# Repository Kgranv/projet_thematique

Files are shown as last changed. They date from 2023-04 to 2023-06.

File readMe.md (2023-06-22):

# Requirements :<br/>

## For Raspberry pi

- Raspberry Pi OS Lite (64-bit)
- Python 3.10
- Python Libraries :
  - numpy 1.22.2
  - pandas 1.4.1
  - feather-format 0.4.1

## For Windows (optional)

- Python 3.10
- Python Libraries :
  - numpy 1.22.2
  - pandas 1.4.1
  - feather-format 0.4.1
  - matplotlib 3.5.2

# RaspberryPi recommendation :<br/>

- RaspberryPi type : RaspberryPi-4 <br/>
- RaspberryPi name : raspberrypi-projetMOON <br/>
- piUser : projetMOON <br/>

# Useful command :<br/>

For windows with powershell :<br/>

- Connect to raspberryPi with SSH :<br/>
  <code>ssh piUser@piName</code><br/>
- Send file to raspberryPi :<br/>
  <code>scp dataToSend piUser@piName:/home/piUser/folderPath</code><br/>
- Retrieve file from raspberryPi :<br/>
  <code>scp piUser@piName:/home/piUser/FilePath localFilePath</code><br/>
  if you are already in localFilePath, replace localFilePath by ".\\"<br/>

For raspberry-pi terminal :<br/>

- View file in directory :<br/>
  <code>ls</code><br/>
- change directory :<br/>
  <code>cd directoryName</code><br/>
  if you want to go in parent folder change directoryName by ..
- remove file :<br/>
  <code>rm fileName</code><br/>
- read file :<br/>
  <code>cat fileToRead</code>
- start pyhton script<br/>
  <code>python script.py</code><br/>
- start experience script<br/>
  <code>nohup python experience.py ftrFile.ftr</code><br/>

# How to setup your raspberry-pi :<br/>

You need to use the Raspberry Pi Imager software available here : https://www.raspberrypi.com/software/<br/>
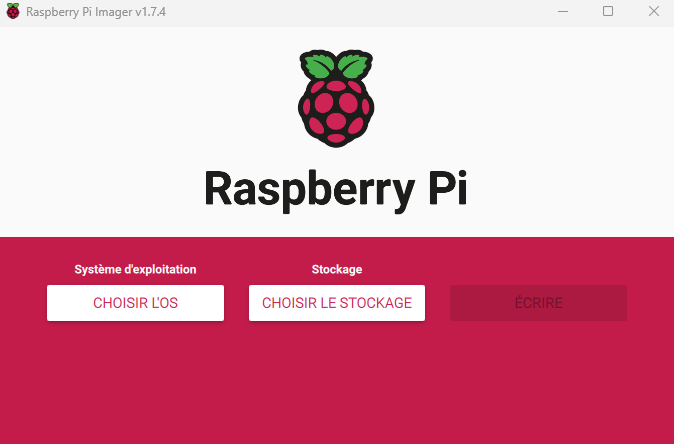
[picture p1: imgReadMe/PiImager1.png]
PiImagerPicture1


## Step 1 : Chose OS

You need to chose the Raspberry Pi OS Lite(64-bit). Don't use 32-bit OS because some library needs a 64-bit OS.<br/>
You can find it in Raspberry Pi OS (other) menu.
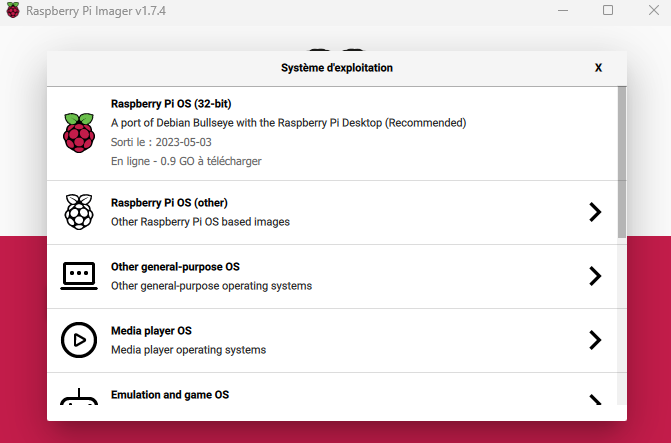
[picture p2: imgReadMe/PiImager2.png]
PiImagerPicture2

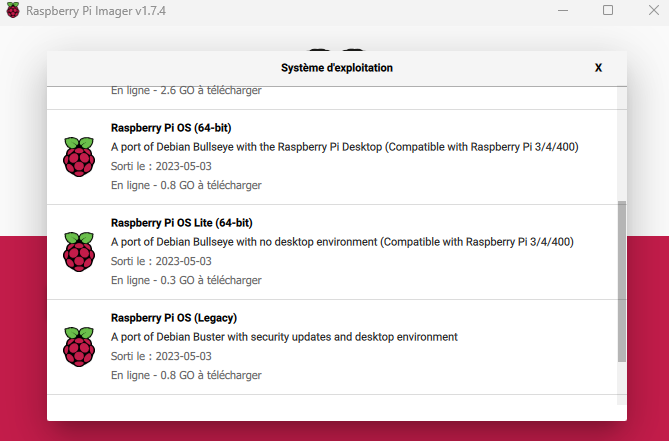
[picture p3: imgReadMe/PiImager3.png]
PiImagerPicture3


## Step 2 : Chose storage

Select the SD card you will use for the raspberry pi.

## Step 3 : Setup advance parameter

You need to change multiple parameter before writing the OS in the SD card :<br/>
You can find the parameter in the gear.<br/>

- Chose for all sessions in Image customization options
- Change the raspberry pi name<br/>
- Activate SSH : <br/>
  use authentification by password<br/>
- Define username and password<br/>
- Configurate the wifi<br/>

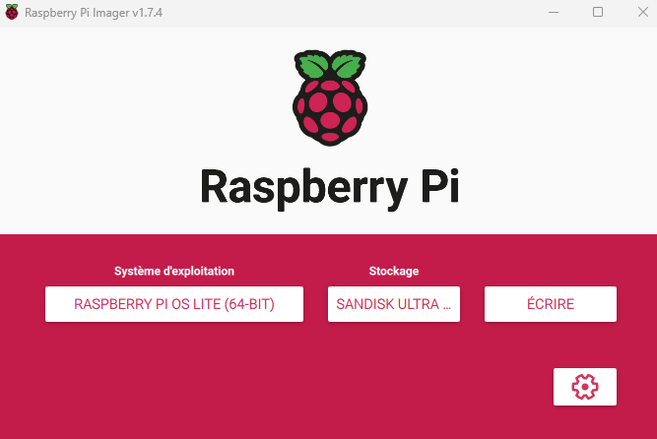
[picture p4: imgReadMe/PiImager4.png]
PiImagerPicture4

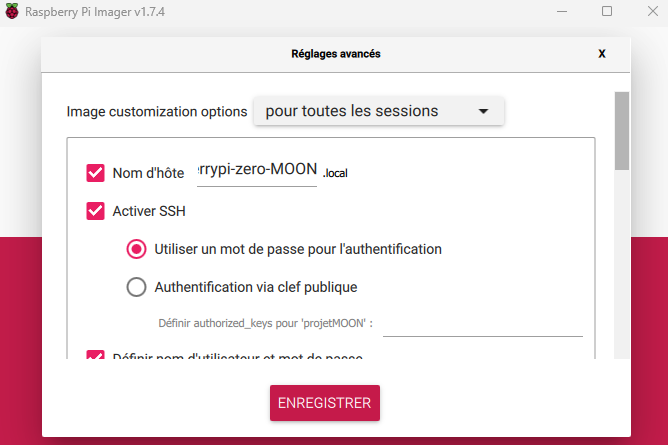
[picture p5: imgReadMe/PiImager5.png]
PiImagerPicture5

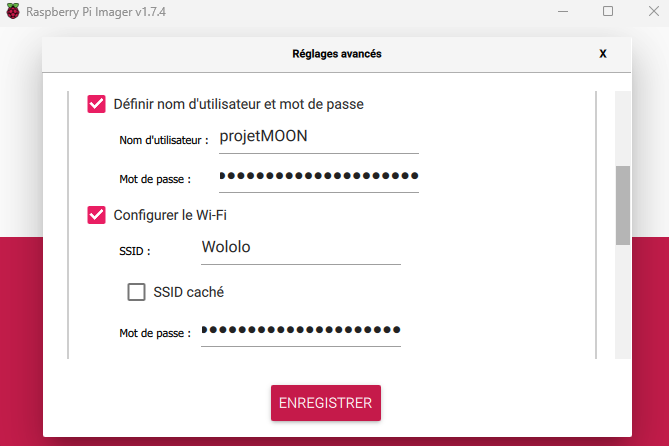
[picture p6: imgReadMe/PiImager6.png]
PiImagerPicture6


## Step 4 : Write on SD card

You can write the OS in the SD card and your OS it's ready !<br/>

## Step 5 : Install dependencies and Setup directory

You need to install dependencies.<br/>

- Connect to your raspberry pi via SSH :<br/>
  <code>ssh piUser@piName</code><br/>
  use the piUser and piName you have setup in step 3.<br/>
- Install OS update :<br/>
  <code>sudo apt update</code><br/>
  <code>sudo apt upgrade</code><br/>
- Install python :<br/>
  <code>sudo apt install python3.10</code>
- Install python library :<br/>
  <code>pip install numpy</code><br/>
  <code>pip install pandas</code><br/>
  <code>pip install feather-format</code><br/>
- Create directory :<br/>
  <code>mkdir data</code><br/>
  <code>mkdir userData</code><br/>

All the dependencies are installed you can close the SSH connection by closing the terminal.<br/>

## Step 6 : Transfert file on raspberry pi

You need to transfert all necessary file on raspberry pi.<br/>
Download following file from the repository :<br/>

- armerPompe.py<br/>
- controle.csv<br/>
- controle.py<br/>
- dataPreparation.py<br/>
- experience.py<br/>
- resetGPIO.py<br/>

repeat the following command for each file in the list to transfert to raspberry pi :<br/>

- Send file to raspberryPi :<br/>
  <code>scp fileToSend piUser@piName:/home/piUser</code><br/>

The setup of the raspberry pi is complete.

# Plug experience

## Motor

### Motor n°1

- red wire to Mosfet 1 Drain
- black wire to Mosfet 1 Source

### Motor n°2

- red wire to Mosfet 2 Drain
- black wire to Mosfet 2 Source

### Motor n°3

- red wire to Mosfet 3 Drain
- black wire to Mosfet 3 Source

## Electrovanne

### Electrovanne n°1

- wires to Mosfet 4 Drain/Source

### Electrovanne n°2

- wires to Mosfet 5 Drain/Source

### Electrovanne n°3

- wires to Mosfet 5 Drain/Source

## Raspberry pin

### Alimentation

- pin 4 (Alimentation 5V) to 5 V
- pin 6 (GND) to GND

### Motor

- pin 11 (GPIO 17) to Mosfet 1 Gate
- pin 13 (GPIO 27) to Mosfet 2 Gate
- pin 15 (GPIO 22) to Mosfet 3 Gate

### Electrovanne

- pin 29 (GPIO 5) to Mosfet 4 Gate
- pin 31 (GPIO 6) to Mosfet 5 Gate
- pin 33 (GPIO 13) to Mosfet 6 Gate

# Run an experience

## Step 1 : Prepare your data

The data need to be in csv file. The separator need to be ",".<br/>
Your data are presented like this :<br/>

| time | conc1 | conc2 |
| :--- | :---- | :---- |
| 0    | 1     | 1     |
| 2    | 6     | 8     |
| 10   | 2     | 1     |
| 15   | 4     | 2     |

time correspond of time from the start in second.<br/>
conc1 and conc2 it's the concentration of element at time t.

If you have download dataPreparation.py on your computer you can convert your data on your computer directly.
For convert your data directly on your computer follow the Step 3 before the Step 2.

## Step 2 : Transfert your data on raspberry pi

Transfert your data on the raspberry pi in the folder userData.<br/>
Open terminal in the folder of your data and use this command :<br/>
<code>scp dataToSend piUser@piName:/home/piUser/userData</code><br/>

If you have convert your data directly on your computer use this command instead :<br/>
<code>scp dataToSend piUser@piName:/home/piUser/data</code><br/>

## Step 3 : Convert your data

### If you have transfert your CSV file on raspberry pi

- Connect to your raspberry pi via SSH :<br/>
  <code>ssh piUser@piName</code><br/>
- run dataPreparation.py :<br/>
  <code>python dataPreparation.py</code><br/>
  Indicate the name of your data when ask.

Your data is now converted and placed in data.<br/>
The data converted is named by the date of creation like this:<br/>
year-moth-day_hourminsec.ftr

you can check the name of the data created in the folder data using :<br/>
<code>cd data</code><br/>
<code>ls</code><br/>
it will show all the data in the folder data.<br/>

### If you want convert your data on Windows

Before convert your data on Windows make sure you have the optionnal requirement on your computer.<br/>
Create 2 folder in directory of dataPreparation.py:<br/>

- userData<br/>
- data<br/>

Put your data to convert in userData folder.<br/>
Run dataPrepartion.py and indicate the name of your data when ask.<br/>
Your data is now converted and placed in data.<br/>
The data converted is named by the date of creation like this:<br/>
year-moth-day_hourminsec.ftr<br/>
You can check the data created using the script verificationFtr.py<br/>
Now you can do Step 2.

## Step 4 : Run experience

For start experience connect to raspberry pi if it's not already done :<br/>
<code>ssh piUser@piName</code><br/>
Run experience.py in background with :<br/>
<code>nohup python experience.py dataToUse.ftr</code><br/>
Close the terminal.<br/>
The Experience is running Step 5 and 6 will show you how to interact with experience.

## Step 5 : Control experience

If you want take sample or make an observation during the experience you need to suspend the process.

- Connect to raspberry pi :<br/>
  <code>ssh piUser@piName</code><br/>
- run controle.py
  <code>python controle.py</code><br/>
- Chose what you want to do :<br/>
  1. Sample<br/>
     For take a sample, you need to indicate which quantity you take.<br/>
  2. Observation<br/>
     For observe the cells.<br/>
  3. Restart cycle<br/>
     When you have finished your sample/observation restart the cycle.<br/>
  4. Log<br/>
     For see the last log of the experience.<br/>
  5. Stop<br/>
     Force stop of the experience if something goes wrong.<br/>
  6. Cancel<br/>
     Close controle.py<br/>

When you have finished dont forget to restart cycle and you can press cancel for close controle.py.<br/>

## Step 6 : Check log

- Connect to raspberry pi :<br/>
  <code>ssh piUser@piName</code><br/>
- Open the log:<br/>
  <code>cat output.log</code><br/>

For debug log use instead :<br/>
<code>cat nohup.out</code><br/>

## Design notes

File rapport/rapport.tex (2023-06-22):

% Basic info about your document: a4 paper, 11pt font size, article style.
\documentclass[a4paper, 11pt]{article}

\usepackage{graphicx} % Enables adding figures
\usepackage[a4paper, margin=18mm]{geometry} % Let's you adjust the margins
\usepackage[T1]{fontenc} % Font helvetica
\usepackage[scaled]{helvet}
\usepackage{authblk} % multiauthor
\usepackage{multirow} % table
\usepackage[table,xcdraw]{xcolor}
\usepackage{float} % position des figures,table
\usepackage[backend=biber,style=numeric,sorting=none]{biblatex} % bibliographie
\usepackage{fancyhdr} % footer
\usepackage{caption} % caption
\usepackage{multicol} % multicolonne
\usepackage{adjustbox}
\usepackage{pdfpages}

%Setup bibliographie
\addbibresource{bibliographie.bib} % utilise bibliographie.bib pour la bibliographie

%Setup figure
\graphicspath{ {./figure/} } % relative path for figure

\renewcommand\familydefault{\sfdefault} % set font for all document
\captionsetup[table]{name=Tableau} % Rename table
\renewcommand*\contentsname{Table des matières} % Rename table of contents
\setlength\parindent{0pt} % remove indent in new line

%Setup Titre, auteur et date
\title{
    \vspace{-2.5cm}
    \centering\\
    \centering\rule{17cm}{0.1mm}\vspace*{0.4in}\\
    \centering Projet thématique MOON}
\renewcommand\Authands{ et } % replace "and" by "et" in author
\author[1]{AYRINHAC Elisa}
\author[2]{DROUIN Clément}
\author[3]{JOUCLARD Charly}
\affil[1]{HEPIA, MT2, elisa.ayrinhac@hes-so.ch}
\affil[2]{HEPIA, MT2, clement.drouin@hes-so.ch}
\affil[3]{HEPIA, MT2, charly.jouclard@hes-so.ch}
\date{28 avril 2023}

%Setup header, footer
\pagestyle{fancy}
\fancyhead{} % clear all header fields
\renewcommand{\headrulewidth}{0pt} % no line in header area
\fancyfoot{} % clear all footer fields
\renewcommand{\footrulewidth}{1pt}
\newcommand{\changefont}{\fontsize{9}{11}\selectfont}
\newcommand{\TheAuthor}{AYRINHAC Elisa, DROUIN Clément, JOUCLARD Charly}
\fancyfoot[C]{\changefont\TheAuthor}
\fancyfoot[R]{\changefont\thepage}
\fancyfoot[L]{\changefont Projet thématique MOON}

\begin{document}

%Entete
\maketitle
\thispagestyle{empty}
\begin{center}
    \rule{\textwidth}{0.1mm}
\end{center}
%Introduction
\vspace{-1cm}
\section*{Introduction}
Ce rapport detail le projet thématique de deuxième année de bachelor
microtechnique de HEPIA option Bio-ingénierie.
Cette année notre cliente, Mme Loussert-Fonta Céline est une biologiste travaillante
sur l'endométriose, une maladie encore
peu connue mais très commune, touchant environ 1 femme sur 10.\\
Cette pathologie se caractérise par le développement du tissu semblable
à l'endomètre hors de l'utérus.
Ces tissus peuvent proliférer dans les organes voisins comme les ovaires;
l'intestin, la vessie ou même les poumons.
Les symptômes varient énormément entre les femmes mais ont retenu, le
plus souvent, celui de la douleur
extrême provoqué par la croissance de ces tissus.\\
Les objectifs du projet sont, d'une part, de mettre en application les
connaissances acquises durant nos études, mais également de développer de
nouvelles compétences comme la gestion de projet.
D'autre part, ce projet contribue à développer la recherche sur
l'endométriose et servira de support pour le \\
"project MOON : endoMetriosis Organoids to vOice up woman paiN".\\
Le but de notre projet est de créer un bio-chip qui permettrait d'étudier
les tissus de l'endomètre in vitro durant un cycle utérin. Cela signifie, imaginer, concevoir, fabriquer,
et tester un dispositif capable se recrée
les conditions d'un utérus (Température, humidité, concentration d'hormones, etc...)
\vspace{1cm}
\maketitle
\thispagestyle{empty}
\begin{center}
    \rule{\textwidth}{0.1mm}
\end{center}
\newpage
%Table des matieres
\tableofcontents
\newpage
%Debut rapport
\section{Etudes préliminaire}
\subsection{Biologie}
\subsubsection{Contexte}
Pour que l'expérience soit optimale, le client a besoin de suivre l'évolution d'un tissu d'endomètre sur la
durée d'un cycle endométrial.
Le système doit être compact et permettre l'observation des cellules en culture ainsi que la possibilité de
collecter des cellules et du milieu de culture pour analyse.
Afin mieux comprendre comment concevoir un appareil correspondant à la demande du client, une courte
introduction biologique est nécessaire.
\subsubsection{L'endomètre}
\begin{figure}[H]
    \centering
    \resizebox{0.5\linewidth}{!}{}
    \caption{Localisation de l'endomètre dans l'utérus}
    \label{fig:Schema_endomètre}
\end{figure}
L'endomètre est un épithélium qui compose une partie de l'appareil reproducteur féminin, il tapisse les
parois de la cavité utérine et est composé de 3 couches :
\begin{itemize}
    \item Le myomètre qui est la fondation de l'endomètre.
    \item la couche basale qui contient les glandes et les tissu conjonctifs.
    \item la couche fonctionnelle.
\end{itemize}
Cette dernière couche est celle qui vois sa taille changer durant le cycle menstruel.
\subsubsection{Le cycle menstruel}
"Le cycle menstruel est l'ensemble des phénomènes physiologiques,
survenant le plus souvent de façon périodique, qui préparent l'organisme de la femme à une éventuelle
fécondation.
La connaissance du cycle menstruel est importante pour aborder l'étude des troubles de la menstruation,
dans l'exploration de l'infertilité et dans la mise en œuvre des techniques de procréation médicalement
assistées."
\cite{Cycle_menstruel}\\
L'hypothèse émise par la biologiste serait qu'il y a corrélation en le cycle hormonal et l'apparition
de kystes dus à l'endométriose.
Durant le cycle utérin, le taux d'hormonal de la femme varie selon les jours. Cela permet
au corps de réguler la période de croissance de l'endomètre, puis de déclencher l'ovation et enfin
S'il n'y a pas eu fécondation, de déclencher les menstruations.
\begin{figure}[H]
    \centering
    \resizebox{0.5\linewidth}{!}{}
    \caption{Graphique montrant le cycle menstruel avec ces variation hormonal et ce que
        cela implique}
    \label{fig:Cycle menstruel}
\end{figure}
Comme vu dans la figure 2, les 4 hormones présentent dans le cycle sont :
\begin{itemize}
    \item La progestérone.
    \item Les estrogéne, notamment l'estradiol.
    \item La LH pour luteinizing hormone.
    \item La FSH pour follicle stimulating hormone.
\end{itemize}
La consigne est de reproduire les cycles de concentration de l'estradiol et de la progestérone.
Car ce sont les hormones suspectées dans l'apparition de l'endométriose. Cela signifie
recrée les conditions d'homéostasie des cellules ainsi que les conditions de
concentration de ce cycle et les appliquer à des cellules in vitro.
Afin de répondre au mieux à cette problématique un état de l'art de la culture
cellulaire sera établie ainsi qu'un inventaire des techniques présentent au campus biotech qui
pourraient être utile dans notre projet.
\newpage
\subsection{Etat de l'art}

\subsubsection{Incubateur}
Actuellement la culture cellulaire est un procédé connu et maitriser par l'Homme qui consiste à placer des cellules dans
un milieu de culture afin de les faire proliférer.
Cette méthode permet d'avoir des colonies de cellule pouvant aller jusqu'à former des organoïdes pouvant être utilisés
à des fins de recherche. Les organoïdes se comportant de manière similaire à l'organe miniaturisé.
Peu importe l'objectif, la méthode de culture garde toujours un objectif d'homéostasie et un objectif de prolifération. Dans la pratique cela revient
à placer dans un incubateur une colonie de cellules contenue dans un milieu nutritif.
Pour maintenir de bonnes conditions on place ces échantillons dans l'enceinte d'un incubateur qui permet d'isoler les cellules du milieu extérieur tout
en maintenant les constantes de températures, d'humidité et de CO2 de façon optimale.
Les incubateurs professionnels sont des machines de précision, asservis qui permettent de régler précisément toutes les conditions de leurs enceintes;
cela permet de chercher l'expression de certains phénotypes au sein des colonies.
Ils sont aussi dotés de sécurités notamment en matière de ventilation afin de protéger les cellules et le biologiste. Toutefois cette précision rend le matériel cher.
Il faut compter entre 5 000 CHF et 15 000 CHF pour un incubateur professionnel.
L'incubateur fait maison sont moins précise mais permette une personnalisation complète en matière de condition de culture.
Toutefois même si cela reste compliqué à construire dans sa totalité, il est assez simple de stabiliser la température et l'humidité.
Ces machines permettant de créer une atmosphère apte à la reproduction cellulaire toutefois il nous faut quelque chose qui contient les cellules et leur milieu nutritif.
il faut des instruments de culture biocompatible.
\subsubsection{Matériau biocompatible}
On appelle matériau biocompatible, les matériaux qui ont la capacité à ne pas interférer;
ne pas dégrader, le milieu biologique dans lequel ils sont utilisés. Dans notre cas, il faut
que le lieu d'accueil des cellules ne dégrade en rien leurs fonctionnements.
Actuellement les zones de culture sont
\begin{itemize}
    \item Les boites de pétris.
    \item Les écouvillons.
    \item La verrerie de chimie.
    \item Dans les labo d'HEPIA à la FCBG des biochip en PMMA, un polymere biocompatible.
\end{itemize}
Cette liste n'est pas exaustive, tout comptenant fait d'un matériau biocompatible peut en théorie
accueillir des cellules.
\subsubsection{Fluidique}
La fluidique est une partie importante dans la survie des cellules, c'est grace à elle que les
nutriments sont acheminés jusqu'à la zone de culture.
Elle se compose de tous les éléments comprenant du fluide, tel que :
\begin{itemize}
    \item Les réservoirs.
    \item Les pompes.
    \item les tuyaux.
    \item les vannes.
\end{itemize}
Les tuyaux utilisés à la FCBG sont de qualités médicales, c'est-à-dire qui sont biocompatibles. Ils ne diffusent pas
dans le milieu de culture, et ils ne sont pas sensibles aux méthodes de stérilisation.
\newpage
\subsection{Aperçu du projet}
\subsubsection{Besoins}
On peut voir avec la figure \ref{fig:bete_corne} que le système conçu va permettre au biologiste d'étudier l'influence des hormones sur du tissu endométrial.
\begin{figure}[H]
    \centering
    \resizebox{\linewidth}{!}{}
    \caption{Bête à corne}
    \label{fig:bete_corne}
\end{figure}
\subsubsection{Fonctions}
\begin{table}[H]
    \centering
    \begin{tabular}{|
            >{\columncolor[HTML]{CBCEFB}}l |l|}
        \hline
        \multicolumn{1}{|c|}{\cellcolor[HTML]{CBCEFB}\textbf{N°}} & \textbf{Fonction}                                 \\ \hline
        FP1                                                       & Maintenir les cellules en vie                     \\ \hline
        FP2                                                       & Intégrer des concentrations spécifiques d'hormone \\ \hline
        FC3                                                       & Observer les cellules au microscope               \\ \hline
        FC4                                                       & Alimenter le système en énergie                   \\ \hline
        FC5                                                       & Réaliser un système autonome                      \\ \hline
        FC6                                                       & Résister au milieu imposer par les cellules       \\ \hline
        FC7                                                       & Utiliser un matériau biocompatible                \\ \hline
        FC8                                                       & Respecter le budget                               \\ \hline
        FC9                                                       & Assurer un cycle de 28 jours                      \\ \hline
    \end{tabular}
    \caption{Fonctions à assurer}
\end{table}
\begin{figure}[H]
    \centering
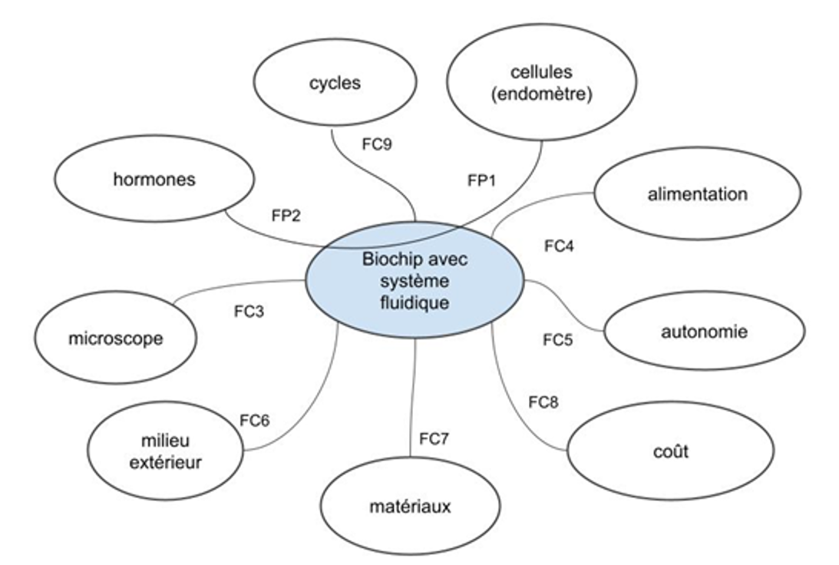
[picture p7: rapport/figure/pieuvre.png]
    \resizebox{\linewidth}{!}{}
    \caption{Diagramme pieuvre avec les fonctions associés}
    \label{fig:pieuvre}
\end{figure}
\subsection{Cahier des charges}
La première fonction à prendre en compte est la survie des cellules.
Pour cela, notre système devra respecter les paramètres suivants :
\begin{itemize}
    \item une température de 37°C
    \item un pH de 7
    \item un renouvellement du milieu de culture de 1 ml par jours
    \item atténué toute variation de milieu
    \item la Biocompatibilité du milieu
\end{itemize}
Pour ce qui est du système fluidique, il permet l'apport du milieu de culture à la cellule et donc nécessite de répondre aux points suivants :
\begin{itemize}
    \item un système étanche
    \item un écoulement laminaire
    \item un système de purge
    \item un système d'injection d'hormones
    \item un mélangeur pour éviter des pics de concentration
    \item une pompe pour un système dynamique
\end{itemize}
Enfin, le système dans sa globalité devra assurer :
\begin{itemize}
    \item une autonomie de 28 jours minimum
    \item une zone transparente permettant l'observation des cellules
\end{itemize}
\subsection{Catalogue de solutions}
\subsubsection{Gestion des nutriments, déchets et de la concentration des hormones}
\begin{table}[H]
    \centering
    \begin{tabular}{|l|l|l|}
        \hline
        \multicolumn{1}{|c|}{\textbf{Solution}}        & \textbf{Avantages}                                                                                                     & \textbf{Inconvénients}                                                                                                             \\ \hline
        Seringues auto-poussés                         & \begin{tabular}[c]{@{}l@{}}-Précis\\ -Facile d'utilisation\\ -Facilement programmable\\ -Réponse linéaire\end{tabular} & \begin{tabular}[c]{@{}l@{}}-Energie\\ -Limité en quantité\\ -Espace\end{tabular}                                                   \\ \hline
        \rowcolor[HTML]{CBCEFB}
        Pompe péristaltiques\cite{pompe_peristaltique} & -Déjà présent au labo                                                                                                  & \begin{tabular}[c]{@{}l@{}}-Peu précis\\ -Energie\end{tabular}                                                                     \\ \hline
        Système de goutte à goutte                     & \begin{tabular}[c]{@{}l@{}}-Low-cost\\ -Economique en énergie\end{tabular}                                             & \begin{tabular}[c]{@{}l@{}}-Précision\\ -A pression atmosphérique\\ -Complexité d'asservissement\\ -Réponse chaotique\end{tabular} \\ \hline
    \end{tabular}
    \caption{Solutions pour la gestions des nutriments, déchets et des hormones}
\end{table}
\subsubsection{Contrôler l'environnement extérieur}
\begin{table}[H]
    \centering
    \begin{tabular}{|l|l|l|}
        \hline
        \multicolumn{1}{|c|}{\textbf{Solution}} & \textbf{Avantages}                                                                                        & \textbf{Inconvénients}                                                                      \\ \hline
        \rowcolor[HTML]{CBCEFB}
        Incubateur                              & \begin{tabular}[c]{@{}l@{}}-Constante externe stable\\ -A disposition\\ -Retour d'expérience\end{tabular} & \begin{tabular}[c]{@{}l@{}}-Placé dans l'incubateur\\ -Protéger l'électronique\end{tabular} \\ \hline
        Système autonome                        & -Pas de dépendance                                                                                        & \begin{tabular}[c]{@{}l@{}}-Compliqué à réaliser\\ -Energivore\\ -Coût\end{tabular}         \\ \hline
    \end{tabular}
    \caption{Solutions pour gérer l'environnement extérieur}
\end{table}
\subsubsection{Cultiver les cellules}
\begin{table}[H]
    \centering
    \begin{tabular}{|l|l|l|}
        \hline
        \multicolumn{1}{|c|}{\textbf{Solution}} & \textbf{Avantages}                                                                                         & \textbf{Inconvénients}                                                             \\ \hline
        \rowcolor[HTML]{CBCEFB}
        Bio-chip en PMMA                        & \begin{tabular}[c]{@{}l@{}}-Usinage\\ -Retour d'expérience\\ -Sur mesure\\ -Fluidique intégré\end{tabular} & \begin{tabular}[c]{@{}l@{}}-Assemblage par couche\\ -Long à fabriquer\end{tabular} \\ \hline
        Boîte de pétris                         & \begin{tabular}[c]{@{}l@{}}-Coût\\ -Stérilité\end{tabular}                                                 & -Pas de circulation de fluide                                                      \\ \hline
    \end{tabular}
    \caption{Solutions pour le milieu de culture}
\end{table}
\subsubsection{Circulation du fluide}
\begin{table}[H]
    \centering
    \begin{tabular}{|l|l|l|}
        \hline
        \multicolumn{1}{|c|}{\textbf{Solution}} & \textbf{Avantages}                                                                                            & \textbf{Inconvénients}                                           \\ \hline
        \rowcolor[HTML]{CBCEFB}
        Pompe péristaltique                     & \begin{tabular}[c]{@{}l@{}}-Déjà présent au labo\\ -Facile d'utilisation\\ -Pas de contamination\end{tabular} & \begin{tabular}[c]{@{}l@{}}-Débit limité\\ -Energie\end{tabular} \\ \hline
        Gravité                                 & \begin{tabular}[c]{@{}l@{}}-Pas besoin de matériel spécifique\\ -Pas besoin d'alimentation\end{tabular}       & -Compliqué à mettre en oeuvre                                    \\ \hline
    \end{tabular}
    \caption{Solutions pour injecter les différents fluides}
\end{table}
\subsubsection{Mélanger les fluides}
\begin{table}[H]
    \centering
    \begin{tabular}{|l|l|l|}
        \hline
        \multicolumn{1}{|c|}{\textbf{Solution}} & \textbf{Avantages}                                                                                                           & \textbf{Inconvénients}                                                                                  \\ \hline
        \rowcolor[HTML]{CBCEFB}
        Mélangeur hydrostatique "2D"            & \begin{tabular}[c]{@{}l@{}}-Economique\\ -Facilité d'intégration\\ -Compact\\ -Volume sur mesure\\ -Modélisable\end{tabular} & \begin{tabular}[c]{@{}l@{}}-A créer\\ -Perte de charge\end{tabular}                                     \\ \hline
        Mélangeur hydrostatique "3D"            & \begin{tabular}[c]{@{}l@{}}-Economique\\ -Facilité d'intégration\\ -Compact\\ -Volume sur mesure\\ -Modélisable\end{tabular} & \begin{tabular}[c]{@{}l@{}}-A créer\\ -Perte de charge\\ -Usinage\end{tabular}                          \\ \hline
        Mélangeur magnétique                    & \begin{tabular}[c]{@{}l@{}}-Déjà présent au labo\\ -Facilement nettoyable\\ -Gestion de la puissance\end{tabular}            & \begin{tabular}[c]{@{}l@{}}-Espace\\ -Biocompatibilité\\ -Non modélisable\\ -Non pilotable\end{tabular} \\ \hline
    \end{tabular}
    \caption{Solutions pour assurer l'homogénéité des liquides}
\end{table}
\subsubsection{Analyser les concentrations}
\begin{table}[H]
    \centering
    \begin{tabular}{|l|l|l|}
        \hline
        \multicolumn{1}{|c|}{\textbf{Solution}} & \textbf{Avantages}                                                                                                                  & \textbf{Inconvénients}                                                                           \\ \hline
        \rowcolor[HTML]{CBCEFB}
        Colorimètre externe                     & \begin{tabular}[c]{@{}l@{}}-Facilité d'intégration\\ -Précis\\ -Déjà présent au labo\end{tabular}                                   & \begin{tabular}[c]{@{}l@{}}-Aucune donnée interne\\ -Nécessite présence utilisateur\end{tabular} \\ \hline
        Colorimètre interne                     & \begin{tabular}[c]{@{}l@{}}-Retour en temps réel\\ -Gain de précision de l'asservissement\\ -Donnée interne au système\end{tabular} & \begin{tabular}[c]{@{}l@{}}-A créer\\ -Précision\end{tabular}                                    \\ \hline
    \end{tabular}
    \caption{Solutions pour contrôler les concentrations}
\end{table}
\subsubsection{Contrôler le système (microcontrôleur)}
\begin{table}[H]
    \centering
    \begin{tabular}{|l|l|l|}
        \hline
        \multicolumn{1}{|c|}{\textbf{Solution}} & \textbf{Avantages}                                                                                                                                      & \textbf{Inconvénients}                                                                                                                           \\ \hline
        Arduino Uno                             & \begin{tabular}[c]{@{}l@{}}-Facilité d'utilisation\\ -Flexible\end{tabular}                                                                             & \begin{tabular}[c]{@{}l@{}}-Pas de stockage interne\\ -Pas de contrôle à distance\\ -Pas de possibilité d'utiliser python\\ -14 pin\end{tabular} \\ \hline
        \rowcolor[HTML]{CBCEFB}
        Raspberry Pi                            & \begin{tabular}[c]{@{}l@{}}-Retour en temps réel\\ -Contrôlable à distance\\ -Stockage interne\\ -Utilisation possible de Python\\ -40 pin\end{tabular} & -Faible disponibilité                                                                                                                            \\ \hline
    \end{tabular}
    \caption{Solutions pour commander le système}
\end{table}
\subsubsection{Alimentation}
\begin{table}[H]
    \centering
    \begin{tabular}{|l|l|l|}
        \hline
        \multicolumn{1}{|c|}{\textbf{Solution}} & \textbf{Avantages} & \textbf{Inconvénients}                                              \\ \hline
        \rowcolor[HTML]{CBCEFB}
        Secteur                                 & -Disponibilité     & -Toujours branché                                                   \\ \hline
        Batteries                               & -Portable          & \begin{tabular}[c]{@{}l@{}}-Prix\\ -Recharge compliqué\end{tabular} \\ \hline
    \end{tabular}
    \caption{Solutions pour alimenter le bio-chip}
\end{table}
\subsection{Schéma bloc du système}
\begin{figure}[H]
    \centering
    \resizebox{\linewidth}{!}{}
    \caption{Schéma bloc du système}
    \label{fig:schema_block}
\end{figure}
\subsection{Choix pour le projet}
Afin de réaliser la culture de cellules de l'endomètre, tout en respectant le cahier
des charges, la conception d'un bio-chip sur-mesure devient une . Pour ce faire on va utiliser différents
outils disponibles dans le laboratoire afin de diminuer les coûts. Certaines pièces devront être
fabriqués afin de répondre au besoin comme le boitier du bio-chip.
Pour accueillir les cellules un boitier en PMMA sera conçu et usiner sur
place grâce à la découpe laser qui se trouve dans le campus.
Pour la régulation de l'environnement l'utilisation d'un incubateur présent dans le laboratoire sera
utilisés pour accueillir les cellules afin de diminuer le cout de fabrication.
Pour la partie commandée, l'utilisation d'un micro-ordinateur type Raspberry pie permettra de contrôler
Les constantes du bio-chip. Pouvant contrôler celui-ci à distance et étant plus puissance, le raspberry a
De multiples avantages face à l'ardu ino UNO.
Pour un apport d'hormones et de nutriment précis les pousses seringues qui sont disponibles
dans le laboratoire, vont être incorporer au système, toutefois l'éventualité d'utiliser des pompes à là
place n'est pas écartée.
Les pompes fournies par HEPIA, pour le projet, permettrons de créer un flux au sein du biochip.
L'ensemble du bio-chip sera alimenté par le secteur afin de limiter les coûts de fabrication et éviter
de devoir développer un système avec une batterie.

\newpage
\section{Conception mécanique}
\subsection{Mélangeur hydrostatique}
\subsubsection{Simulation fluidique}
Dans cette partie porté sur la simulation et de la modélisation d'un mélangeur statique
permettant de rendre le mélange homogène avant de l'envoyer sur les cellules.
Afin de déterminer la forme du mélangeur une courte recherche a été faite sur la simulation fluide de créo.
Dans l'industrie, les mélangeurs statiques sont des composants de fluidique en 3 dimensions conçue pour
perturber l'écoulement et ainsi créé des turbulences.
Cela a pour but de mélanger le fluide sans utiliser de composant actif tel qu'une pompe, un moteur;
ou un mélangeur magnétique.
\begin{figure}[H]
    \centering
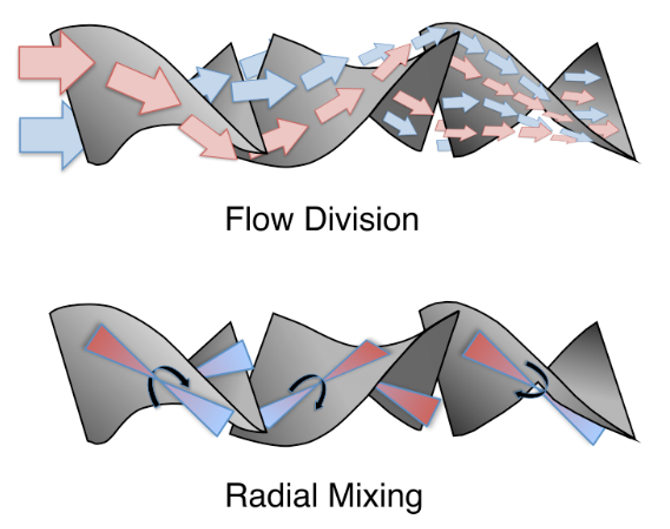
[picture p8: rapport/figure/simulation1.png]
    \resizebox{0.4\linewidth}{!}{}
    \caption{Schéma montrant comment ce mélange un fluide}
    \label{fig:simulation1}
\end{figure}
Une première étape de conception fut donc d'essayer de comprendre à quoi pourrait bien ressembler ce
type de mélangeur en 2D.
On sait de par la mécanique des fluides que la pression et la vitesse d'écoulement sont liée à la
géométrie du milieu d'écoulement. Ainsi pour mélanger les fluides il faut "perturber" le flux afin de faire
varier la vitesse de manière hétérogène.
Ainsi différents mélangeurs ont été modélisés afin d'observer le comportement du fluide alors
d'une simulation.
De plus le mode de fabrication le plus simple étant la découpe LASER il a fallu adapter la forme
de ceux-ci afin qu'il soit réalisable en entier à la découpeuse LASER du campus.
\newline
\begin{multicols}{2}
    \begin{figure}[H]
        \centering
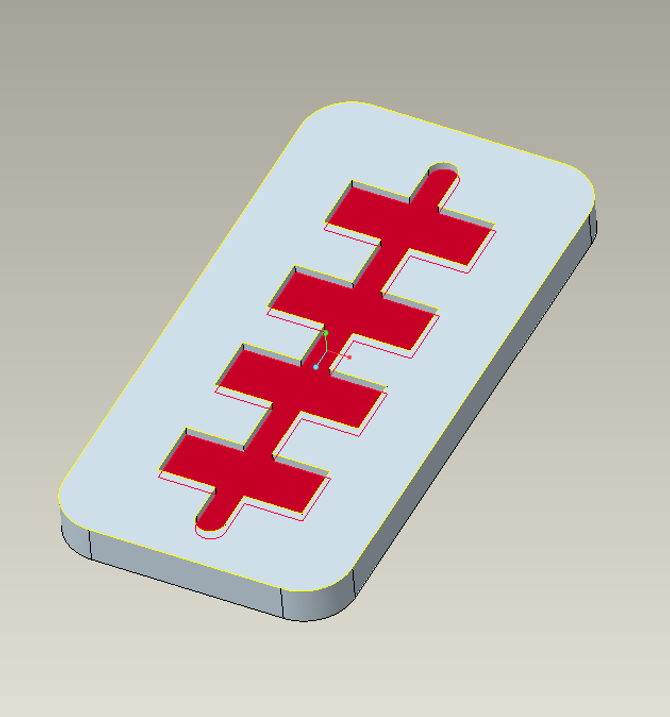
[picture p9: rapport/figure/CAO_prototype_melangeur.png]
        \resizebox{0.95\linewidth}{!}{}
        \caption{CAO du mélangeur avec chicanes}
        \label{fig:CAO_prototype_melangeur}
    \end{figure}
    \begin{figure}[H]
        La figure \ref{fig:CAO_prototype_melangeur} montre la première étape de recherche;
        le premier mélangeur était juste composé d'un chemin direct auquel ont été ajoutées
        des cavités latérales.
        Le flux de liquide assimilé à de l'eau dans la simulation entre par en dessous et sort par au-dessus;
        et les conditions de pression sont celles données dans la datasheet de la pompe, étant donné
        que le mélangeur sera placé juste derrière la pompe.
    \end{figure}
\end{multicols}
\newpage
\begin{multicols}{2}
    \begin{figure}[H]
        \centering
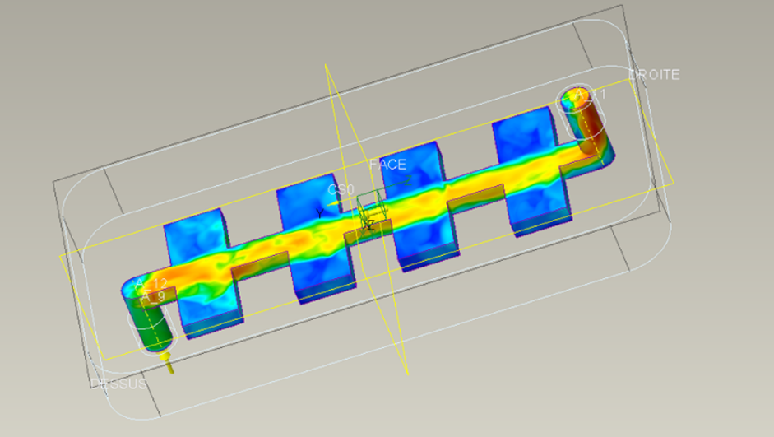
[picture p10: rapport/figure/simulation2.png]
        \resizebox{0.95\linewidth}{!}{}
        \caption{Première simulation fluidique}
        \label{fig:simulation2}
    \end{figure}
    \begin{figure}[H]
        La figure \ref{fig:simulation2} montres un résultat de simulation.
        Les couleurs représentent la vitesse du flux de liquide, ici la simulation avait juste pour but de
        tester les fonctionnalités de créo. Toutefois il y a des zones (en bleu) ou le liquide est statique
        et des zones (Orange) ou le liquide ses deplace plus rapidement.
        L'idée a ensuite été de séparer le flux en deux et de les recombiner pour créer des turbulences.
        Une autre version avait pour idée de détendre et de comprimer le flux afin de créer des
        turbulences.
    \end{figure}
\end{multicols}

\begin{figure}[H]
    \centering
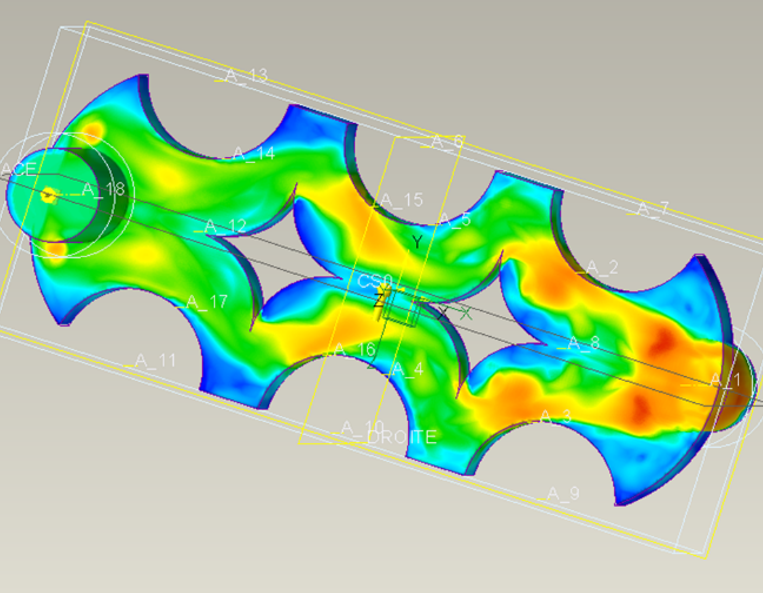
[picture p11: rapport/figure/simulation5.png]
    \resizebox{0.5\linewidth}{!}{}
    \caption{Simulation fluidique avec chicanes et obstacles}
    \label{fig:simulation5}
\end{figure}
La figure \ref{fig:simulation5} montre l'importance de placer un obstacle au centre du flux, de plus la variation
de section vient ajouter des perturbations. C'est ce schéma qui est retenu pour la forme du mélangeur.
Les variations de section vont être accentuées et le bloc central sera en un seul morceau afin de facilité les
découpes.
Le principe de montage repose sur celui deja utilisé dans les laboratoires de HEPIA. Le melangeur sera composé de 3
couches;
\begin{itemize}
    \item Une première couche servant de socle, dotée de trous dans lesquels des goupilles pourront etres insérées.
    \item Une couche centrale contenant la forme du mélangeur, c'est-à-dire les bords et le centre.
    \item Une dernière couche permettant de refermer le mélangeur et de fixer les raccords de fluidique.
\end{itemize}
\newpage

\subsubsection{CAO du mélangeur}
Apres plusieurs simulations, les choix se sont tourné vers un mélangeur comportant l'entrée et la sortie de chaque
coté du mélangeur. Le flux est séparer en deux par la partie centrale, puis les flux sont accélérés séparément parréduction
de la section découlement. Des zones plus vaste, (contenant plus de liquide) sont laiser colontairement afin de profoqué un diférence de vitesse
entre le liquide présent dans ces zones et celui qui arrive. Enfin le chemin fluide n'est composée que de partie de courbe,
cela permet de limiter l'apparition de bulles.
\begin{multicols}{2}
    \begin{figure}[H]
        \centering
        \resizebox{\linewidth}{!}{}
        \caption{Couche central du mélangeur}
        \label{fig:CAO_melangeur_couche2}
    \end{figure}
    \begin{figure}[H]
        \centering
        \resizebox{\linewidth}{!}{}
        \caption{Mélangeur hydrostatique}
        \label{fig:CAO_melangeur}
    \end{figure}
\end{multicols}
Notre conception est basée sur un principe de sandwich, une première épaisseur permettant l'étanchéité, le support et le guidage des autres couches.
Une couche centrale munit d'un détrompeur composer d'un élément externe guider par deux goupilles extérieures, et un élément interne guidé par les goupilles intérieures.
Et enfin une dernière couche permettant de fermer le tout, toujours guider par les deux goupilles externes.
L'adhésion et l'étanchéité sera assuré par une couche adhésive déposer sur les plaques.
\subsection{Zone de culture}
\begin{figure}[H]
    \centering
    \resizebox{0.5\linewidth}{!}{}
    \caption{bio-chip pour les cellules}
    \label{fig:CAO_cellule}
\end{figure}
Pour le biochip contenant les cellules visibles sur la figure \ref{fig:CAO_cellule}, nous avons choisi d'utiliser l'assemblage en plusieurs couches de PMMA.
Celui-ci contient 4 couches d'épaisseur différentes pour répondre à certaines contraintes.
Nous utiliserons des goupilles, pour être sûr que les différents éléments soient bien alignés.

\newpage
\begin{multicols}{2}
    \begin{figure}[H]
        \centering
        \resizebox{\linewidth}{!}{}
        \caption{CAO de la première couche}
        \label{fig:CAO_cellule_couche1}
    \end{figure}
    \begin{figure}[H]
        \centering
        \resizebox{\linewidth}{!}{}
        \caption{CAO de la seconde couche}
        \label{fig:CAO_cellule_couche2}
    \end{figure}
\end{multicols}
La couche du dessous fait 0.3 mm d'épaisseur pour facilité l'observation des cellules au microscope.
La 2e couche est prévu pour contenir les cellules mais sera supprimer car elle crée des angles droits qui risque d'endommager les cellules.
\begin{multicols}{2}
    \begin{figure}[H]
        \centering
        \resizebox{\linewidth}{!}{}
        \caption{CAO de la troisième couche}
        \label{fig:CAO_cellule_couche3}
    \end{figure}
    \begin{figure}[H]
        \centering
        \resizebox{\linewidth}{!}{}
        \caption{CAO de la quatrième couche}
        \label{fig:CAO_cellule_couche4}
    \end{figure}
\end{multicols}
La 3e couche permet au fluide contenant les hormones et nutriment de circuler la où seront accroché les cellules.
L'entrée du fluide est plus étroite que la sortie pour éviter des problèmes de surpression.
Et enfin la dernière couche contient les trous pour chasser les connecteur Luer lock, permettant de relier le bio chip contenant les cellules au reste du système par l'intermédiaire de tuyaux.
Les angles devront être arrondit pour éviter d'endommager les cellules.
\subsection{Support des réservoirs}
Désormais le rendu physique projet devient très claire,
celui-ci sera composer d'un boitier auxquelles sera fixé les trois pompe,
les quatre tube comprenant les hormones, le liquide de culture neuf, et usagé.
Ce boitier sera lui aussi découper au LASER et au besoin renforcé par des pièces
imprimé en 3D.
Il ne contiendra pas l'électronique, celui-ci sera placer en dehors de l'incubateur
et relier au système via un câble.
Il est à noter qu'il manque les électrovannes, qui ont été modéliser et qui seront
placer de l'autre côté des pompes.
\begin{multicols}{2}
    \begin{figure}[H]
        \centering
        \resizebox{\linewidth}{!}{}
        \caption{CAO du porte réservoir version 1}
        \label{fig:CAO_reservoir1}
    \end{figure}
    \begin{figure}[H]
        \centering
        \resizebox{\linewidth}{!}{}
        \caption{CAO du porte réservoir version 2}
        \label{fig:CAO_reservoir2}
    \end{figure}
\end{multicols}
\begin{figure}[H]
    \centering
    \resizebox{0.4\linewidth}{!}{}
    \caption{CAO des électrovannes}
    \label{fig:CAO_electrovanne}
\end{figure}
\subsubsection{Le boitier découpable au LASER}
Le boitier à été concus pour etre entièrment découper au LASER. Pour cela chaque face du boitier à été modélisé de facon à se qu'elle s'emboite entre elles une fois assemblé.
Pour des questions de maintient, 8 petites équerres de maintient à visser ont été concus
et les plaques serons collées entre elles par de la colle à plexiglass.
On peut aussi imaginer ne pas fixer une des plaque mais la vissée et placer un joint papier.
Cela permettrais d'avoir la possibilité d'ouvrir le boitier sans le casser.
\begin{figure}[H]
    \centering
    \resizebox{\linewidth}{!}{}
    \caption{CAO du boitier à découper au LASER}
    \label{fig:CAO_boitier_decoupe_LASER}
\end{figure}
De plus, deux support à imprimer en 3D,ont été ajoutées pour fixer le melangeur et
la zone de culture.
Ces support permettrons de fixer la zone de culuture et de pouvoir la retirer pour
faire des observation.

\newpage
\subsection{Assemblage des biochips}
Pour réaliser l’assemblage du mélangeur et du biochip qui contiendra les cellules,
la première étapes a été de découper chaque éléments dans des plaques de PMMA.
Afin de facilité l’assemblage, seul la couche du milieu est recouverte de colle
sur ces deux faces. La deuxième étape consiste à assembler le tout.
Les goupilles du gabarit (voir figure \ref{fig:gabarit}) permettent l’alignement
des 3 différentes couches. Une fois les 3 couches superposer,
il faut s’assurer que celle-ci sont correctement collé entre elles.
Pour cela, les trois couches sont pressé entre elles à l’aide d’un rouleau.
Enfin, les luer-lock sont emboiter dans le boichip avec de la colle époxy.
\begin{multicols}{3}
    \begin{figure}[H]
        \centering
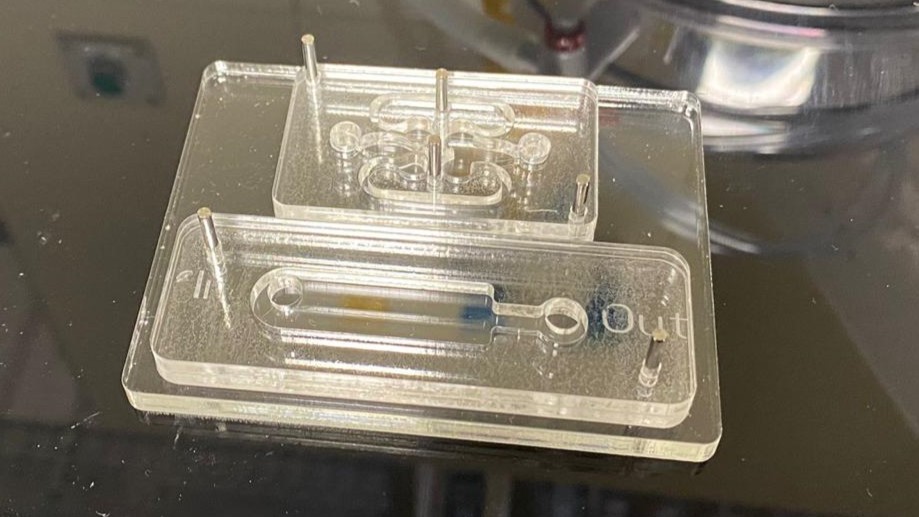
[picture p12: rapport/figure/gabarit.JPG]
        \resizebox{\linewidth}{!}{}
        \caption{Photo du gabarit et des biochips}
        \label{fig:gabarit}
    \end{figure}
    \begin{figure}[H]
        \centering
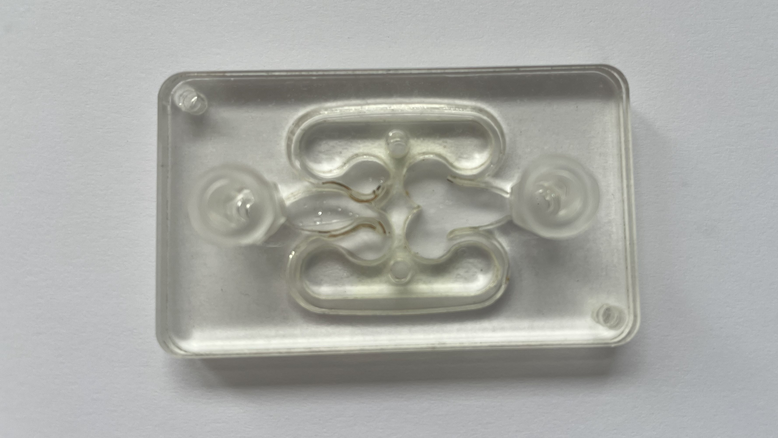
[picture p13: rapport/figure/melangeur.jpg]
        \resizebox{\linewidth}{!}{}
        \caption{Photo de l'assembage du mélangeur}
        \label{fig:melangeur}
    \end{figure}
    \begin{figure}[H]
        \centering
        \resizebox{\linewidth}{!}{}
        \caption{Photo de l'assembage du biochip cellules}
        \label{fig:cellules}
    \end{figure}
\end{multicols}
\subsubsection{Le biochip cellules}
\begin{multicols}{2}
    \begin{figure}[H]
        \centering
        \resizebox{\linewidth}{!}{}
        \caption{Photo du test fluidique}
        \label{fig: fluide_cellules}
    \end{figure}
    \begin{figure}[H]
        \centering
        \resizebox{\linewidth}{!}{}
        \caption{Photo des restes de liquide}
        \label{fig:reste_cellules}
    \end{figure}
\end{multicols}
Après avoir injecté du fluide dans le biochip, celui-ci ne fuit pas.
Cependant, le test a montré une mauvaise optimisation de l'espace.
En effet, comme le montre la photo de la figure 4, le liquide reste
bloqué à certains endroits. Pour optimiser la circulation du fluide,
une nouvelle version de ce biochip a été modélisée.
\newpage
\subsubsection{Modelisation biochip cellules version 2}
\begin{multicols}{2}
    \begin{figure}[H]
        \centering
        \resizebox{\linewidth}{!}{}
        \caption{CAO assemblage biochip cellules V2}
        \label{fig: CAO_cellulesV2}
    \end{figure}
    \begin{figure}[H]
        \centering
        \resizebox{\linewidth}{!}{}
        \caption{CAO milieu du biochip cellules V2}
        \label{fig:milieu_cellulesV2}
    \end{figure}
\end{multicols}
Les entrées et sorties du fluide ont le même diamètre que les trous pour insérer les embouts luer-lock, afin d'éviter d'avoir une zone inutile autour de ces embouts.
De plus, pour la zone plus large qui accueillera les cellules, les angles à 90° ont été remplacés par des angles à 45°. Cela devrait éviter la formation de bulles d'air.
\subsubsection{Le mélangeur}
Les premiers tests du mélangeur ont été effectués en faisant circuler du liquide à l'intérieur, à l'aide de seringues.
\begin{figure}[H]
    \centering
    \resizebox{\linewidth}{!}{}
    \caption{Photo test fluidique mélangeur}
    \label{fig:fuite_melangeurV1}
\end{figure}
Comme on peut observer sur la \label{fig:fuite_melangeur} le liquide s'infiltre dans l'intercouche ce qui cause une fuite
par un trou de fabrication.
\subsubsection{CAO mélangeur version 2}
Le premier mélangeur fuyait, cela était probablement dû à une surpression qui causait
l'infiltration du liquide dans l'intercouche. Ainsi dans l'optique de pouvoir commencer
Le test le plus rapidement possible, un nouveau mélangeur, plus simple, a été modéliser.
Celui-ci a pour but d'être plus solide, d'être encore usinable au LASER, et d'utiliser un volume moindre.
\begin{multicols}{2}
    \begin{figure}[H]
        \centering
        \resizebox{\linewidth}{!}{}
        \caption{Premiere couche du melangeur V2}
        \label{fig: CAO_melangeur_V2_couche1}
    \end{figure}
    \begin{figure}[H]
        \centering
        \resizebox{\linewidth}{!}{}
        \caption{Deuxième couche du mélangeur V2}
        \label{fig:CAO_melangeur_V2_couche2}
    \end{figure}
\end{multicols}
L'idée de séparer puis de refusionner le flux est rester
sauf que le chemin est bien plus simple et les bords sont toujours
arrondits. Une section reduite permet une accélation du flux.
Les dimensions on été agrandi afin d'avoir 1cm de chaque coté ce
qui est deux fois plus que l'ancien.
\begin{multicols}{2}
    \begin{figure}[H]
        \centering
        \resizebox{\linewidth}{!}{}
        \caption{Dernière couche du melangeur V2}
        \label{fig: CAO_melangeur_V2_couche3}
    \end{figure}
    \begin{figure}[H]
        \centering
        \resizebox{\linewidth}{!}{}
        \caption{L'assemblage du mélangeur V2}
        \label{fig:CAO_melangeur_V2}
    \end{figure}
\end{multicols}
Le nouveau mélangeur remplace l'ancien ainsi la piece
permettant la fixation du mélangeur au boitier à donc été ajusté.
\subsubsection{CAO boitier version 2}
\begin{figure}[H]
    \centering
    \resizebox{\linewidth}{!}{}
    \caption{Boitier modifier pour accueillir le melangeur V2}
    \label{fig:CAO_boitier_V2}
\end{figure}
La figure \ref{fig:CAO_boitier_V2} montre le rendu final du prototype, il reste alors à le découper et à l'assembler.
\newpage
\section{Conception électronique et programmation}
\subsection{Carte d'alimentation version 1}
\begin{figure}[H]
    \centering
    \resizebox{\linewidth}{!}{}
    \caption{Montage électronique pour l'alimentation du Raspberry Pi et des pompes version 1}
    \label{fig:CAO_electronique_V1}
\end{figure}
L'alimentation de tous le biochip se fera via l'alimentation d'un Arduino de 60 W.
Il arrive sur la carte d'alimentation via la connectique circulaire JAlim.
U1 est un régulateur de tension à découpage de la marque TRACO, il permet de descendre la tension de 12V à 5V il sert à alimenter le Raspberry pi qui sera alimenter par ses pins GPIO.
Les moteurs seront contrôlés par les mosfet M1, M2 et M3.
Les moteurs seront branchés à la carte via des connecteurs circulaire afin que le système soit le plus flexible possible.
Les diodes D1, D2 et D3 sont des diodes de roues libres.
\newpage
\subsubsection{Carte d'alimentation version 2 et 3}
Lorsque nous avons testé la première version du circuit électronique nous avons remarqué que le montage ne fonctionnait pas.
En effet nous avons remarqué que le raspberry pi ne fournit pas assez de tension aux mosfets pour alimenter les pompes.
Pour pouvoir alimenter correctement les pompes une tension de 3,5 V est nécessaire à la "gate" des mosfets.
Cependant le raspberry pi ne peut fournir qu'une tension de 3,3 V via les pins qui sont contrôlables.
\begin{figure}[H]
    \centering
    \resizebox{\linewidth}{!}{}
    \caption{Montage électronique pour l'alimentation du Raspberry Pi et des pompes version 2}
    \label{fig:CAO_electronique_V2}
\end{figure}
Pour obtenir la tension adéquate nous avons amplifié le signal grâce à un AOP pour pouvoir piloter les pompes.
Les AOP devaient être alimentés via le 12 V du transformateur.
Après plusieurs essais infructueux nous avons remarqué que les AOP que nous avons choisies ne peuvent être alimentées par une alimentation non-symétrique.
En alimentant les amplificateurs via une alimentation de laboratoire stabilisé avec une tension symétrique +5/-5 V le montage fonctionnait correctement.
\begin{figure}[H]
    \centering
    \resizebox{\linewidth}{!}{}
    \caption{Montage électronique pour l'alimentation du Raspberry Pi et des pompes version 3}
    \label{fig:CAO_electronique_V3}
\end{figure}
Nous avons récupéré de nouveau amplificateurs qui sont compatibles en alimentation non-symétrique, pour éviter de devoir alimenter une partie du montage via une alimentation de laboratoire.
\subsubsection{Carte d'alimentation version 4}
\begin{figure}[H]
    \centering
    \resizebox{\linewidth}{!}{}
    \caption{Montage électronique pour l'alimentation du Raspberry Pi, des pompes et des électrovannes version 4}
    \label{fig:CAO_electronique_V4}
\end{figure}
Lors des essais, l'électronique ce comportait comme attendu. Voici donc la version final de l'électronique qui comprend le contrôle des électrovannes.
Le contrôle des électrovannes se fait de la même manière que les pompes.
\subsection{Programmation}
\subsubsection{GitHub}
On a mis en place un GitHub pour se partager les codes de programmation, le "repo" contient aussi le guide d'utilisateur.
Il est disponibles ici : https://github.com/Kgranv/projet\_thematique
\subsubsection{Raspberry Pi}
Le Raspberry pi 4 est paramétré pour qu'on puisse se connecter dessus à distance à l'aide du protocole SSH.
L'utilisateur peut s'y connecter facilement dessus à partir du moment que l'on se trouve sur le même réseau wifi.
Il peut lui transmettre des fichiers ainsi que récupérer des fichiers qui sont stockées dessus.
\subsubsection{Préparation des données}
Ce code permet de préparer les datas afin de pouvoir être utiliser par le logiciel qui contrôle le biochip.
Il a été conçu pour que l'utilisateur rentre un minimum de donner afin de gagner du temps.
Il permet de convertir un fichier csv que l'utilisateur aura créée au préalable avec les différents jalons de concentration en un fichier qui contient toutes les concentrations de l'expérience sur 28 jours.
Sur la figure \ref{fig:dataPreparation} on peut voir une représentation des données rentrées par l'utilisateur et les données produites par le programme.
\begin{figure}[H]
    \centering
    \resizebox{\linewidth}{!}{}
    \caption{Données généré par le programme avec les données rentrées par l'utilisateur}
    \label{fig:dataPreparation}
\end{figure}
L'utilisateur peut l'utiliser directement sur un ordinateur puis envoyer le fichier généré sur le Raspberry pi ou bien on peut envoyer le fichier csv sur le Raspberry pi puis le généré directement sur le Raspberry pi.
Le fichier généré est un fichier de type ftr il n'est donc pas lisible directement ceci est fait afin de gagner en rapidité d'exécution et gagner du stockage.
Si on utilisait un fichier csv équivalent il contiendrait tellement de donnés qu'il faudrait plusieurs secondes pour le généré et il prendrait 10 fois plus de stockage.
Le fichier à préparer doit être présenter sous la forme :
\begin{table}[H]
    \centering
    \begin{tabular}{lll}
        Time & Conc1 & Conc2 \\
        0    & 1     & 1     \\
        2    & 6     & 8     \\
        10   & 2     & 1     \\
        15   & 4     & 2
    \end{tabular}
\end{table}
\subsubsection{Programme pour vérifier les fichier ftr}
Ce programme permet d'avoir une prévisualisation des fichiers converti pour vérifier si cela correspond à ce que l'utilisateur veut. Ce programme est fait pour fonctionner sur l'ordinateur de l'utilisateur.
\subsubsection{Programme de test des moteurs}
Un code python permet de vérifier si le contrôle des moteurs fonctionne bien.
En plus de ça il permet d'effectuer les tests de débits des pompes.
Normalement il faudrait environ 30 minutes pour pouvoir tester les débits de toutes les pompes sur une plage de tension d'alimentation des pompes de 6 V à 12 V.
Le code qui permet de contrôler les pompes sera le même que celui dans le programme principal.
\subsubsection{Programme pour armer les pompes}
Ce programme permet d'armer les pompes afin de vider le circuit de toute bulles d'air.
\subsubsection{Programme de l'expérience}
Comme le programme devra tourner pendant 28 jours, il a fallu penser au programme pour qu'il puisse tourner en arrière-plan. En effet, si on coupe la connexion SSH avec le Raspberry Pi, cela coupe les programmes qui sont liés au terminal.
L'une des problématiques est que si on lance un programme en arrière-plan, on ne peut plus lui passer d'input et on ne peut plus voir les outputs du programme.
Pour pallier à ce problème, le programme va lire un fichier CSV afin de recevoir les inputs : controle.csv.
Ses outputs sont redirigés vers 2 fichiers, nohup.out et output.log. Le premier reçoit tous les outputs du programme, qui peuvent servir lors d'éventuels débogages, tandis que le deuxième contient uniquement ceux liés à l'expérience.
Le fichier de contrôle doit être modifié par le programme de contrôle afin d'éviter les bugs.
Dans son fonctionnement, le programme va effectuer plusieurs tâches. Sa tâche principale est de lire le fichier de concentration et de réguler les pompes afin d'atteindre les concentrations désirées.
Il va lire le fichier de contrôle en parallèle pour voir si l'utilisateur ne souhaite pas interagir avec le système.
S'il reçoit une interruption via le fichier de contrôle, il va effectuer en priorité les actions de l'utilisateur, comme par exemple couper les pompes et isoler les cellules pour une observation.
\subsubsection{Programme de contrôle}
Le programme de contrôle permet de contrôler le programme de l'expérience. Il est conçu pour fonctionner sur le Raspberry Pi.
Comme il n'a pas besoin d'être en arrière-plan, on peut interagir avec lui via le terminal.
Son but est de transmettre les ordres de l'utilisateur en écrivant sur le fichier de contrôle : controle.csv.
Une fois que l'utilisateur a fini de transmettre ses ordres, il peut simplement fermer la connexion SSH avec le Raspberry Pi.
L'utilisateur peut transmettre un ordre pour arrêter immédiatement l'expérience s'il y a un problème.
\subsubsection{Programme pour reset les GPIO}
Ce programme permet de reset les pins GPIO si elles ont été utilisés par un autre programmes afin d'avoir la bonne configuration.
\newpage
\section{Maquette final}
Cette dernière partie est une présentation du prototype final.
\subsection{Conception du chassis}
Le chassis utilisés ne sera pas celui présenter precedement car ce projet n'a besoins
d'une maquette fonctionnelle, il s'aggit un projet visant à démontrer que
le systeme fonctionne. La maquette n'ira pas dans l'incubateur, elle n'as pas
besoin d'être étanche.
Ainsi une CAO d'une maquette plus simple a été réaliser puis usiner.
\begin{multicols}{2}
    \begin{figure}[H]
        \centering
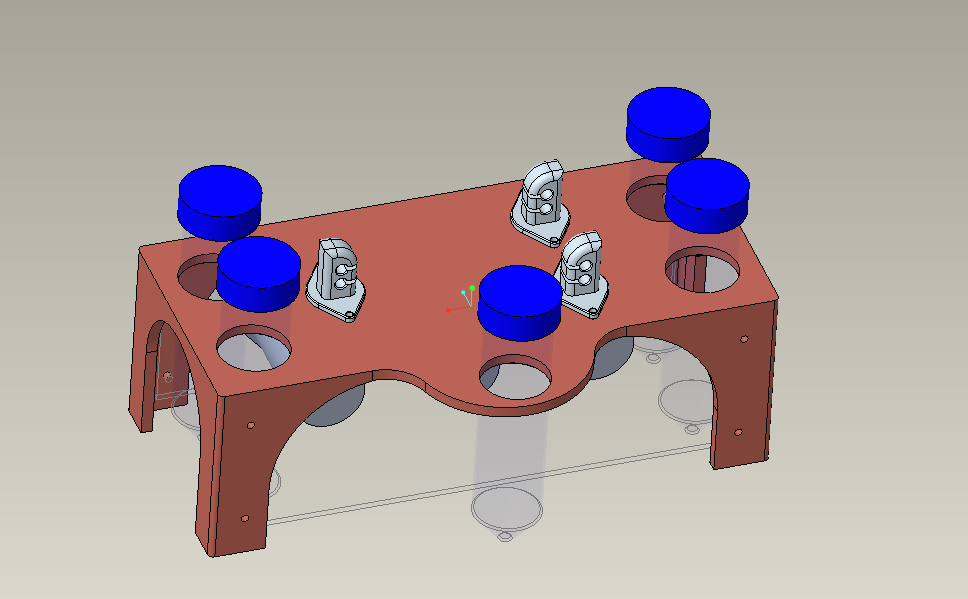
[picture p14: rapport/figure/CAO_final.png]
        \resizebox{0.95\linewidth}{!}{}
        \caption{CAO final}
        \label{fig:CAO_final}
    \end{figure}
    \begin{figure}[H]
        \centering
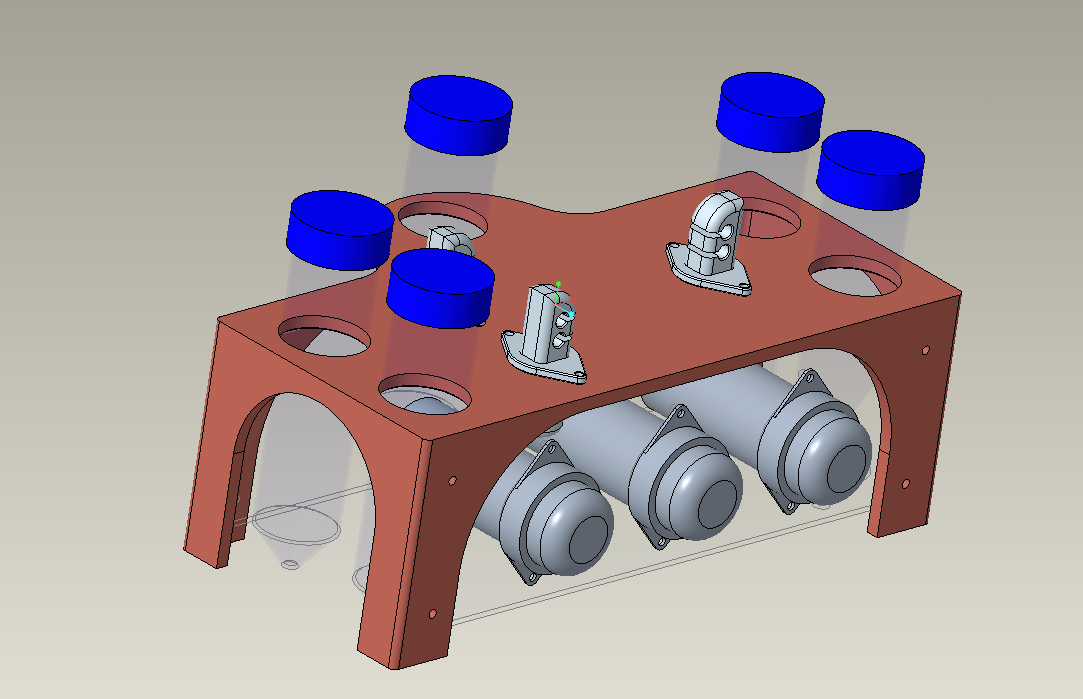
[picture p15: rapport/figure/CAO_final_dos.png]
        \resizebox{0.95\linewidth}{!}{}
        \caption{CAO final vue des moteurs}
        \label{fig:CAO_final_dos}
    \end{figure}
\end{multicols}
Le châssis a été pensé pour être imprimable en 3D, la structure est renforcée avec deux
plaque de PMMA découper au LASER de 3 mm d'épaisseur. La structure est montée grace à
des vis M3 et des écrous. Une des Pâques latérales sera usinée afin d'accueillir les pompes.
Les électrovannes seront fixées sur la partie imprimée en 3D et fixées avec des vis M2.
Le plus grand changement réside dans l'abandon du mélangeur découper au LASER, en effet un 5éme réservoir a été ajouté pour servir de mélangeur. Celui-ci sera muni d'une entrée "compte-gouttes" qui
Consistera en un en bout monté sur le bouchon sans tube venant tomber dans le réservoir.
Pour la sortie il s'agira d'un tube allant au fond du mélangeur.
Le mélangeur fonctionnera comme une perfusion médicale, ce genre de dispositif est très efficace
mais possède une constante de temps de mélange relativement grande, celle-ci dépendant en
grande partie du volume engagé dans le système.
\newpage
\begin{figure}[H]
    \centering
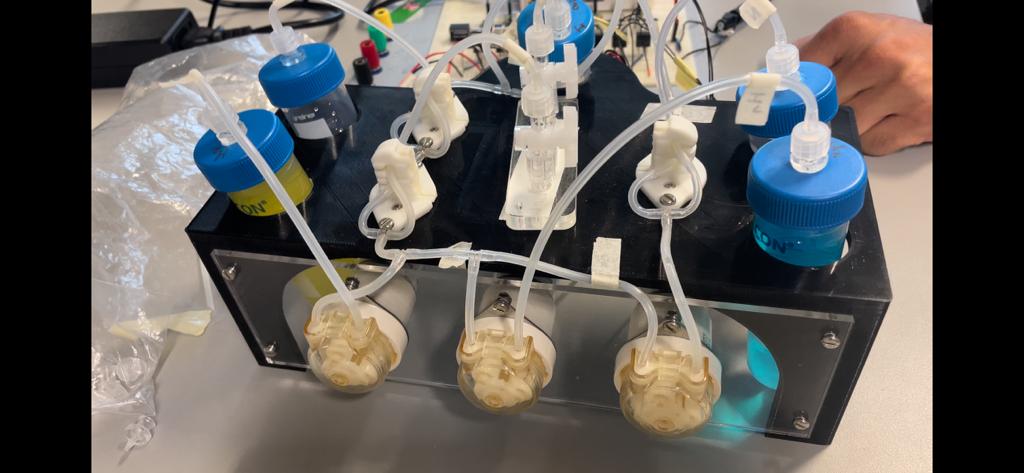
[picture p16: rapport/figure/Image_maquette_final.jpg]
    \resizebox{0.95\linewidth}{!}{}
    \caption{Maquette final}
    \label{fig:Maquette}
\end{figure}
La maquette finale représenter dans la figure \ref{fig:Maquette} est celle qui sera présenté
à la fin de notre projet.
On y retrouve les réservoirs, les électrovannes et toute la fluidique. Le biochip est juste posé sur le système
il aurait pu être fixer au châssis avec des goupilles. Cependant dû aux nombreuse manipulations
le choix fut de le laisser comme cela. \\
Une vue du dessus permet de bien comprendre le fonctionnement du prototype.
\begin{figure}[H]
    \centering
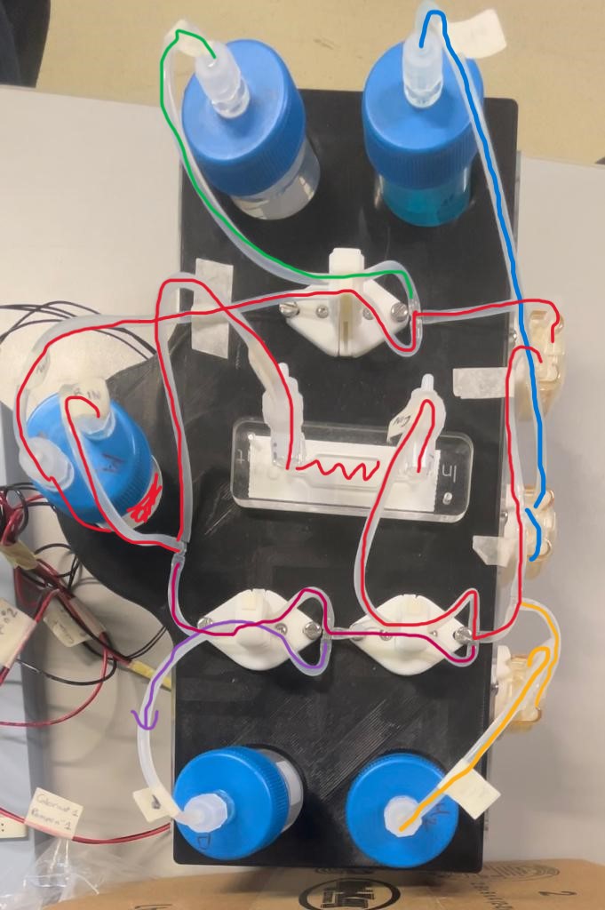
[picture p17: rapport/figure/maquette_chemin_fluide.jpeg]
    \resizebox{0.95\linewidth}{!}{}
    \caption{Explication de la fluidique.}
    \label{fig:Maquette_flu}
\end{figure}
\begin{itemize}
    \item En rouge, le circuit principal, toujours en mouvement grace à la pompe c'est lui qui maintient l'apport en nutriments.
    \item En Jaune et en bleu, les injecteurs d'hormones, conçues avec des pompes peristatiques.
    \item À Magenta, le bipass de la zone de culture, permettant d'éviter un choc de concentration en attendant que le mélange ce fasse.
    \item En violet, le reservoir de purge.
\end{itemize}
\newpage
\section{Conclusion}
La réalisation de ce projet a permis de mettre à profit nos connaissances afin de concevoir un système permettant de soumettre des cellules à un cycle de concentration d'hormones spécifique. Ce projet nous a enseigné les outils de gestion de projet, ce qui nous a conduit au développement du prototype final. Tout au long de ce projet en groupe, nous avons tiré des leçons de nos erreurs, améliorant ainsi notre efficacité.
\newline
Pour accueillir les cellules, nous avons conçu un biochip en PMMA, associé à un circuit fluidique. Ce circuit est composé de pompes et d'électrovannes, permettant de reproduire de manière contrôlée le cycle de concentration d'hormones.
\newline
L'ensemble du système est intégré dans un boîtier réalisé en impression 3D et en PMMA. Une version étanche de ce boîtier a été développée pour protéger les pompes et les électrovannes lorsqu'elle est placée dans l'incubateur, tandis que l'électronique de contrôle est placée en dehors de l'incubateur.
\newline
L'électronique est commandée par un Raspberry Pi 4. L'utilisateur peut interagir avec le système depuis son ordinateur grâce à la connexion WiFi. Il a ainsi la possibilité de transmettre un fichier CSV contenant des concentrations spécifiques, ce qui rend le système modulable et adaptable selon ses préférences.
\newline
Le prototype réalisé est fonctionnel, mais des améliorations peuvent être envisagées pour le rendre encore plus performant. Par exemple, la conception d'une carte PCB dédiée et d'un boîtier externe pour l'électronique contribuerait à améliorer la fiabilité et la robustesse du système.
\newline
En conclusion, ce système de fluidique offre une solution fonctionnelle pour soumettre des cellules à un cycle de concentration d'hormones spécifique. Des améliorations peuvent être envisagées pour améliorer les performances.

\newpage

\includepdf[pages={1-11}]{../GuideUtilisateur.pdf}
%
%\newpage
\printbibliography

\end{document}

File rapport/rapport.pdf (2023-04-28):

## Projet thématique MOON

AYRINHAC Elisa¹

, DROUIN Clément² et JOUCLARD Charly³

1HEPIA, MT2, elisa.ayrinhac@hes-so.ch
2HEPIA, MT2, clement.drouin@hes-so.ch 3HEPIA, MT2, charly.jouclard@hes-so.ch

28 avril 2023

## Introduction

Le projet thématique viens se placer dans le cadre des études de bachelor en microtechnique option Bioingénierie. Cette année notre cliente est une biologiste travaillant sur l’endométriose, une maladie encore peu connue touchant 1 femme sur 10. Cette pathologie se caractérise par le développement de tissu semblable à l’endomètre hors de l’utérus. Ces tissus peuvent proliférer dans les organes voisins comme les ovaires, l’intestins, la vessie ou même les poumons. Les symptômes varient énormément entre les femmes mais ont retiens, le plus souvent, celui de la douleur extrême provoquer par la croissance de ces tissus. Le but de notre projet est de créer un bio-chip qui permettrait d’étudier les tissus de l’endomètre soumis à différentes concentration d’hormones.

## Table des matières

1 Etudes préliminaire | 3
1.1 Biologie | | 3
1.2 Etat de l’art | | 3
1.3 Aperçu du projet | | 4
1.3.1 Besoins | | 4
1.3.2 Fonctions | | 4
1.4 Cahier des charges | | 5
1.5 Catalogue de solutions | | 6
1.5.1 Gestion des nutriments, déchets et de la concentration des hormones | | 6
1.5.2 Contrôler l’environnement extérieur | | 6
1.5.3 Cultiver les cellules | | 6
1.5.4 Circulation du fluide | | 6
1.5.5 Mélanger les fluides | | 7
1.5.6 Analyser les concentrations | | 7
1.5.7 Contrôler le système (microcontrôleur) | | 7
1.5.8 Alimentation | | 8
1.6 Schéma bloc du système | | 8
1.7 Déroulé du projet | | 9
1.8 Choix pour le projet | | 9
2 Conception mécanique | 10
2.1 Mélangeur hydrostatique | 10
2.1.1 Simulation fluidique | 10
2.1.2 CAO du mélangeur | 14
2.2 Zone de culture | 15
2.3 Support des réservoirs | 16
3 Conception électronique et programmation | 18
3.1 Carte d’alimentation | 18
3.2 Programmation | 18
3.2.1 GitHub | 18
3.2.2 Raspberry Pi | 18
3.2.3 Préparation des données | 18
4 Conclusion | 20
5 Annexe | 21
Projet thématique MOON | AYRINHAC Elisa, DROUIN Clément, JOUCLARD Charly | 2

## 1 Etudes préliminaire

### 1.1 Biologie

Pour que l’expérience soit optimale, le client a besoin de suivre l’évolution d’un tissu d’endomètre sur la durée d’un cycle endométrial. Le système doit être compact et permettre l’observation des cellules en culture ainsi que la possibilité de collecter des cellules et du milieu de culture pour analyse. Afin mieux comprendre comment concevoir un appareil correspondant à la demande du client, une courte introduction biologique est nécessaire. L’endomètre est un épithélium qui compose une partie de l’appareil reproducteur féminin, il tapisse les parois de la cavité utérine et est composé de 3 couches : Le myomètre qui est la fondation de l’endomètre, la couche basale qui contient les glandes et les tissu conjonctifs et la couche fonctionnelle. Cette dernière couche est celle qui vois sa taille changer durant le cycle menstruel qui est réglé par 4 Hormones. L’hypothèse émise par la biologiste serais qu’il y a une influence du cycle hormonale sur l’apparition de l’endométriose. Il y a notamment deux hormones qui sont suspecter, l’estradiol et la progestérone. Nous allons donc devoir recrée les concentrations de ce cycle et les appliquer à des cellules in-vitro.

### 1.2 Etat de l’art

Actuellement la culture cellulaire est un procédé connu et maitriser par l’Homme qui consiste à placer des cellules dans un milieu de culture afin de les faire proliférer. Cette méthode permet d’avoir des colonies de cellule pouvant aller jusqu’a formé des organoïdes. Organoïdes pouvant être utilisés à des fins de recherche sur l’organe miniaturisé. La méthode d’incubation consiste à placer dans un incubateur une colonie de cellules contenue dans un milieu nutritif. Pour maintenir de bonnes conditions on place ces échantillons dans l’enceinte d’un incubateur qui permet d’isoler les cellules du milieu extérieur tout en maintenant les constantes de températures, d’humidité et de CO2 de façon optimal. Les incubateurs professionnels sont des machines de précision, asservis qui permettent de réglée précisément toutes les conditions de leurs enceinte, cela permet de chercher l’expression de certain phénotype au seins des colonies. Ils sont aussi dotés de sécurité notamment en termes de ventilation afin de protège les cellules et le biologiste. Toutefois cette précision rend le matériel chère. Il faut compter entre 5000CHF et 15000 CHF pour un incubateur professionnel. L’incubateur fait maison sont moins précis mais permette une personnalisation complète en termes de condition de culture. Toutefois même si cela reste compliqué à construire dans sa totalité, il est assez simple de stabiliser la température et l’humidité. Ces machines permettent de crée une atmosphère apte à la reproduction cellulaire toutefois afin de contenir les cellules et leurs milieu nutritif il faut des instruments de culture. L’écouvillons : Il s’agit de petit tube munis d’un couvercle étanche en plastique dans lequel on place un peu de liquide du fait de leurs petite taille et de leurs facilités de conception ils peuvent être alignés afin de facilité la reproductivité toutefois il ne possède aucune capacité permettant de maintenir l’homéostasie de la cellule. La verrerie de chimie : On peut utiliser techniquement tout contenant biocompatible.

Projet thématique MOON | AYRINHAC Elisa, DROUIN Clément, JOUCLARD Charly | 3

### 1.3 Aperçu du projet

### 1.3.1 Besoins

On peut voir avec la figure 1 que le système conçu va permettre au biologiste d’étudier l’influence des hormones sur du tissus endométrial.

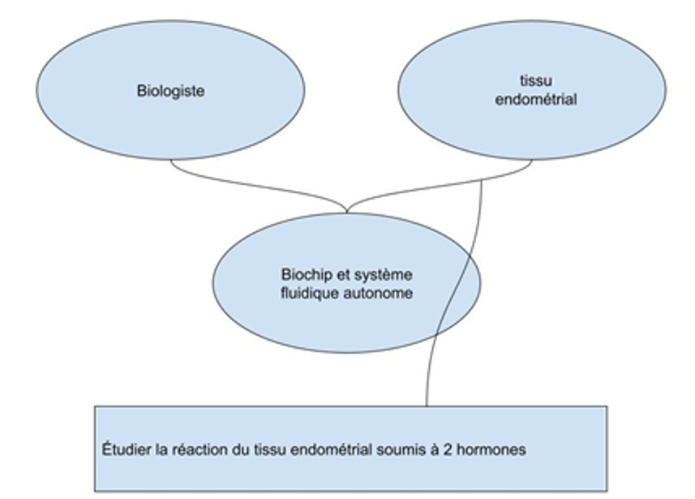
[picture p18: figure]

Figure 1: Bête à corne

### 1.3.2 Fonctions

N° | Fonction
FP1 | Maintenir les cellules en vie
FP2 | Intégrer des concentrations spécifiques d’hormone
FC3 | Observer les cellules au microscope
FC4 | Alimenter le système en énergie
FC5 | Réaliser un système autonome
FC6 | Résister au milieu imposer par les cellules
FC7 | Utiliser un matériau biocompatible
FC8 | Respecter le budget
FC9 | Assurer un cycle de 28 jours

Tableau 1: Fonctions à assurer

Projet thématique MOON | AYRINHAC Elisa, DROUIN Clément, JOUCLARD Charly | 4

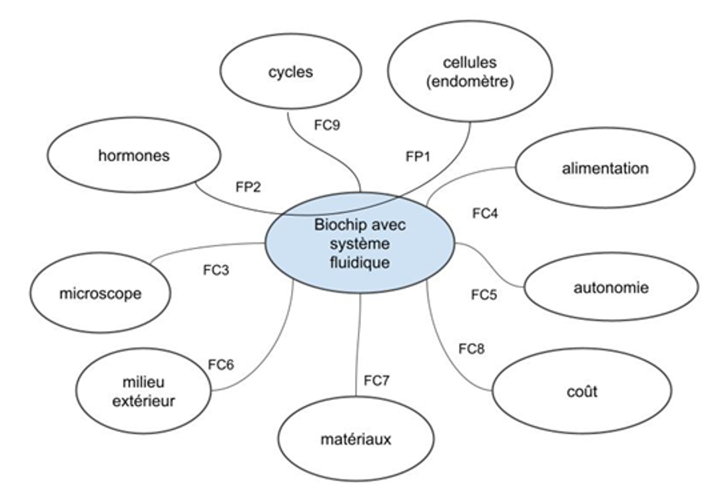
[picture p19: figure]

Figure 2: Diagramme pieuvre avec les fonctions associés

### 1.4 Cahier des charges

La première fonction à prendre en compte est la survie des cellules. Pour cela, notre système devra respecter les paramètres suivants :

- une température de 37°C
- un pH de 7
- un renouvellement du milieu de culture de 1 ml par jours
- atténué toute variation de milieu
- la Biocompatibilité du milieu

Pour ce qui est du système fluidique, il permet l’apport du milieu de culture à la cellule et donc nécessite de répondre aux points suivants :

- un système étanche
- un écoulement laminaire
- un système de purge
- un système d’injection d’hormones
- un mélangeur pour éviter des pics de concentration
- une pompe pour un système dynamique

Enfin, le système dans sa globalité devra assurer :

- une autonomie de 28 jours minimum
- une zone transparente permettant l’observation des cellules
Projet thématique MOON | AYRINHAC Elisa, DROUIN Clément, JOUCLARD Charly | 5

### 1.5 Catalogue de solutions

### 1.5.1 Gestion des nutriments, déchets et de la concentration des hormones

Solution | Avantages | Inconvénients
Seringues auto-poussés | -Précis -Facile d’utilisation -Facilement programmable -Réponse linéaire | -Energie -Limité en quantité -Espace
Pompe péristaltiques[1] | -Déjà présent au labo | -Peu précis -Energie
Système de goutte à goutte | -Low-cost -Economique en énergie | -Précision -A pression atmosphérique -Complexité d’asservissement -Réponse chaotique

Tableau 2: Solutions pour la gestions des nutriments, déchets et des hormones

### 1.5.2 Contrôler l’environnement extérieur

Solution | Avantages | Inconvénients
Incubateur | -Constante externe stable -A disposition -Retour d’expérience | -Placé dans l’incubateur -Protéger l’électronique
Système autonome | -Pas de dépendance | -Compliqué à réaliser -Energivore -Coût

Tableau 3: Solutions pour gérer l’environnement extérieur

### 1.5.3 Cultiver les cellules

Solution | Avantages | Inconvénients
Bio-chip en PMMA | -Usinage -Retour d’expérience -Sur mesure -Fluidique intégré | -Assemblage par couche -Long à fabriquer
Boîte de pétris | -Coût -Stérilité | -Pas de circulation de fluide

Tableau 4: Solutions pour le milieu de culture

### 1.5.4 Circulation du fluide

Solution | Avantages | Inconvénients
Pompe péristaltique | -Déjà présent au labo -Facile d’utilisation -Pas de contamination | -Débit limité -Energie
Gravité | -Pas besoin de matériel spécifique -Pas besoin d’alimentation | -Compliqué à mettre en oeuvre

Tableau 5: Solutions pour injecter les différents fluides

Projet thématique MOON | AYRINHAC Elisa, DROUIN Clément, JOUCLARD Charly | 6

### 1.5.5 Mélanger les fluides

Solution | Avantages | Inconvénients
Mélangeur hydrostatique "2D" | -Economique -Facilité d’intégration -Compact -Volume sur mesure -Modélisable | -A créer -Perte de charge
Mélangeur hydrostatique "3D" | -Economique -Facilité d’intégration -Compact -Volume sur mesure -Modélisable | -A créer -Perte de charge -Usinage
Mélangeur magnétique | -Déjà présent au labo -Facilement nettoyable -Gestion de la puissance | -Espace -Biocompatibilité -Non modélisable -Non pilotable

Tableau 6: Solutions pour assurer l’homogénéité des liquides

### 1.5.6 Analyser les concentrations

Solution | Avantages | Inconvénients
Colorimètre externe | -Facilité d’intégration -Précis -Déjà présent au labo | -Aucune donnée interne -Nécessite présence utilisateur
Colorimètre interne | -Retour en temps réel -Gain de précision de l’asservissement -Donnée interne au système | -A créer -Précision

Tableau 7: Solutions pour contrôler les concentrations

### 1.5.7 Contrôler le système (microcontrôleur)

Solution | Avantages | Inconvénients
Arduino Uno | -Facilité d’utilisation -Flexible | -Pas de stockage interne -Pas de contrôle à distance -Pas de possibilité d’utiliser python -14 pin
Raspberry Pi | -Retour en temps réel -Contrôlable à distance -Stockage interne -Utilisation possible de Python -40 pin | -Faible disponibilité

Tableau 8: Solutions pour commander le système

Projet thématique MOON | AYRINHAC Elisa, DROUIN Clément, JOUCLARD Charly | 7

### 1.5.8 Alimentation

Solution | Avantages | Inconvénients
Secteur | -Disponibilité | -Toujours branché
Batteries | -Portable | -Prix -Recharge compliqué

Tableau 9: Solutions pour alimenter le bio-chip

### 1.6 Schéma bloc du système

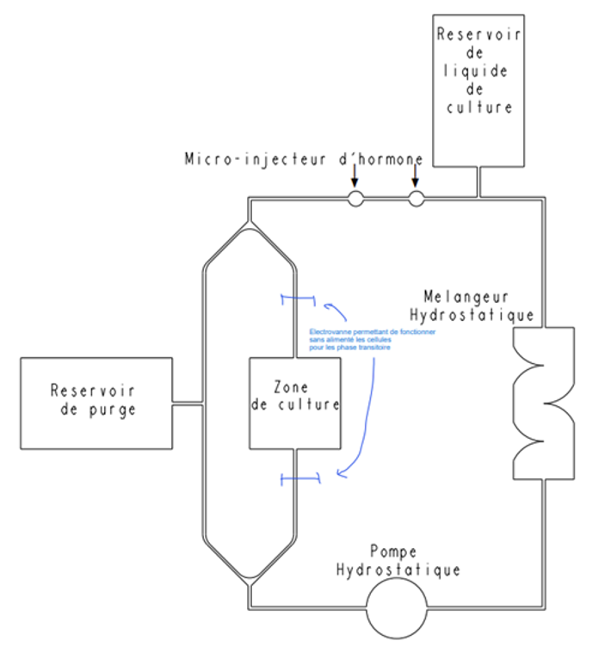
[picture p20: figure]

Figure 3: Schéma bloc du système

Projet thématique MOON | AYRINHAC Elisa, DROUIN Clément, JOUCLARD Charly | 8

### 1.7 Déroulé du projet

insert diagramme de gant

### 1.8 Choix pour le projet

Nous estimons que pour réaliser la culture de cellule de l’endomètre, tout en respectant le cahier des charges, il faut concevoir notre propre bio-chip. Pour ce faire on va utiliser différents outils disponibles dans le laboratoire afin de diminuer les coûts. Certaines pièces devront être fabriqués afin de répondre à nos besoins comme le boitier de notre bio-chip. Pour accueillir nos cellules nos utiliserons un boitier en PMMA que nous fabriquerons sur place grâce à la découpe laser qui se trouve dans le campus. Pour la régulation de l’environnement on utilisera un incubateur présent dans le laboratoire car cela diminuera le cout de fabrication. Nous utiliserons un Raspberry pi pour contrôler notre bio-chip car il dispose de beaucoup plus d’avantage que l’Arduino UNO et il nous permettra de contrôler notre bio-chip à distance. Pour l’apport d’hormones et de nutriment on utilisera des pousses seringues qui sont disponible dans le laboratoire. Pour faire circuler le fluide dans notre boitier on prendra des pompes péristaltiques qui sont fournis. L’ensemble du bio-chip sera alimenté par le secteur afin de limiter les coûts de fabrication et éviter de devoir développer un système avec une batterie

Projet thématique MOON | AYRINHAC Elisa, DROUIN Clément, JOUCLARD Charly | 9

## 2 Conception mécanique

### 2.1 Mélangeur hydrostatique

### 2.1.1 Simulation fluidique

Dans cette partie nous allons parler de la simulation et de la modélisation d’un mélangeur statique permettant de rentre le mélange homogène avant de l’envoyer sur les cellules. Afin de déterminer la forme du mélangeur nous avons basé nos recherches sur la simulation fluide de créo. Dans l’industrie, les mélangeurs statiques sont des composant de fluidique en 3 dimensions conçue pour perturber l’écoulement et ainsi crée des turbulences. Cela a pour but de mélanger le fluide sans utiliser de composant actif tel qu’une pompe, un moteur, ou un mélangeur magnétique.

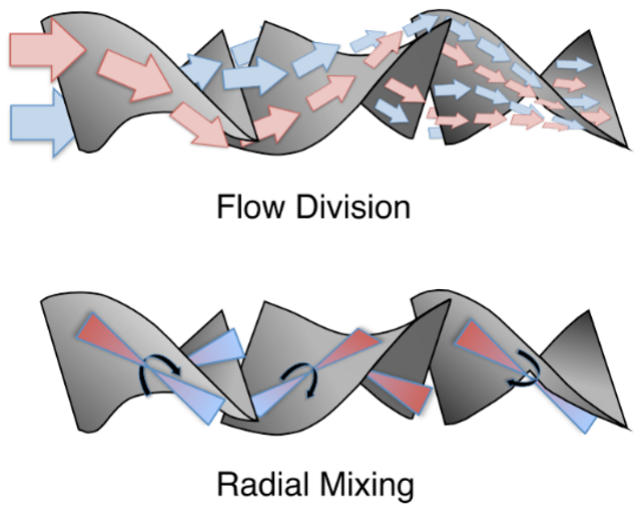
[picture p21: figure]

Figure 4: Schéma montrant comment ce mélange un fluide

Une première étape de conception fus donc d’essayer de comprendre à quoi pourrais bien ressembler ce type de mélangeur en 2D. On sait de par la mécanique des fluides que la pression et la vitesse d’écoulement sont liée à la géométrie du milieu d’écoulement. Ainsi J’ai modélisé quatre différents mélangeurs afin d’observer le comportement du fluide lors d’une simulation. De plus le mode de fabrication le plus simple étant la découpe LASER il a fallu adapter la forme de ceux-ci afin qu’il soit réalisable en entier à la découpeuse LASER du campus.

Projet thématique MOON | AYRINHAC Elisa, DROUIN Clément, JOUCLARD Charly | 10


Figure 5: CAO du mélangeur avec chicanes

Comme on peut le voir dans la figure 5 le premier mélangeur était juste composé d’un chemin direct auquel ont été ajouté des chicanes droites. Le flux de liquide assimiler a de l’eau entre par en dessous et sort par au-dessus, et les conditions de pression sont celle donnée dans la datasheet de la pompe étant donné que le mélangeur sera placer juste derrière la pompe.

Projet thématique MOON | AYRINHAC Elisa, DROUIN Clément, JOUCLARD Charly | 11

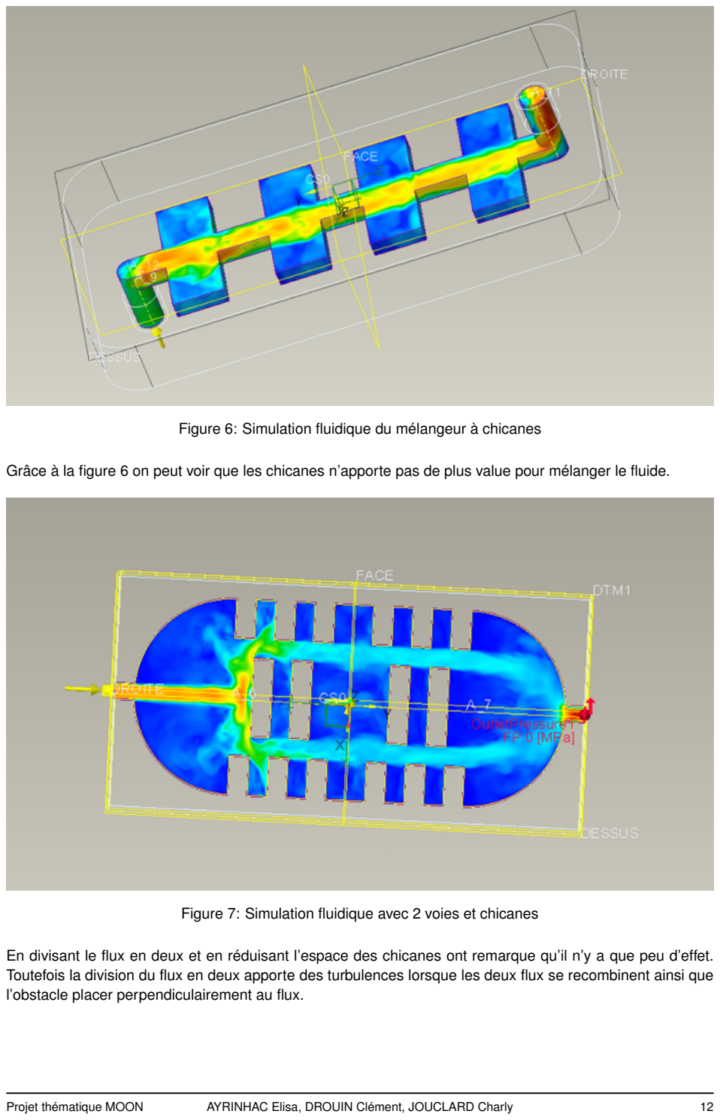
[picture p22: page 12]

Figure 6: Simulation fluidique du mélangeur à chicanes

Grâce à la figure 6 on peut voir que les chicanes n’apporte pas de plus value pour mélanger le fluide.

Figure 7: Simulation fluidique avec 2 voies et chicanes

En divisant le flux en deux et en réduisant l’espace des chicanes ont remarque qu’il n’y a que peu d’effet. Toutefois la division du flux en deux apporte des turbulences lorsque les deux flux se recombinent ainsi que l’obstacle placer perpendiculairement au flux.

Projet thématique MOON | AYRINHAC Elisa, DROUIN Clément, JOUCLARD Charly | 12

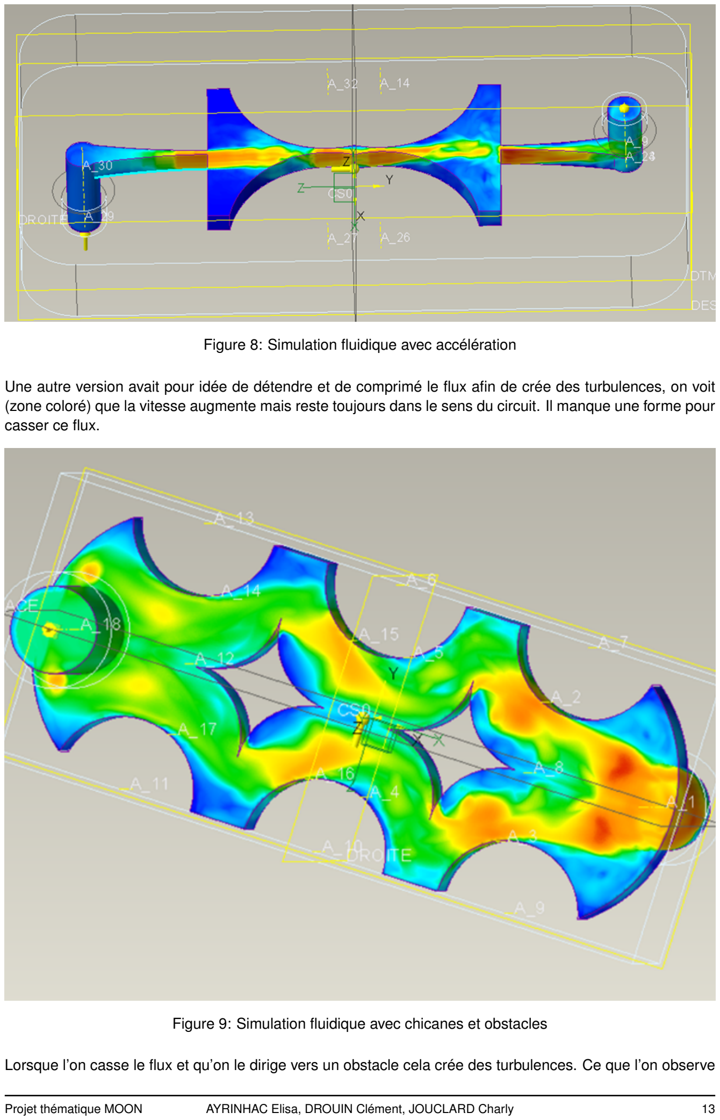
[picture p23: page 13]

Figure 8: Simulation fluidique avec accélération

Une autre version avait pour idée de détendre et de comprimé le flux afin de crée des turbulences, on voit (zone coloré) que la vitesse augmente mais reste toujours dans le sens du circuit. Il manque une forme pour casser ce flux.

Figure 9: Simulation fluidique avec chicanes et obstacles

Lorsque l’on casse le flux et qu’on le dirige vers un obstacle cela crée des turbulences. Ce que l’on observe

Projet thématique MOON | AYRINHAC Elisa, DROUIN Clément, JOUCLARD Charly | 13

ici c’est une accélération du fluide couplé à des zone de dépression. Cela cause des turbulences derrière les obstacles placer au centre.

### 2.1.2 CAO du mélangeur

Nous avons donc choisi de partir sur un mélangeur composé de deux parties, l’une central permet de casser de flux et de le séparer en deux. La partie externe est mobilisé afin de crée des zones d’accélération et de décélération.

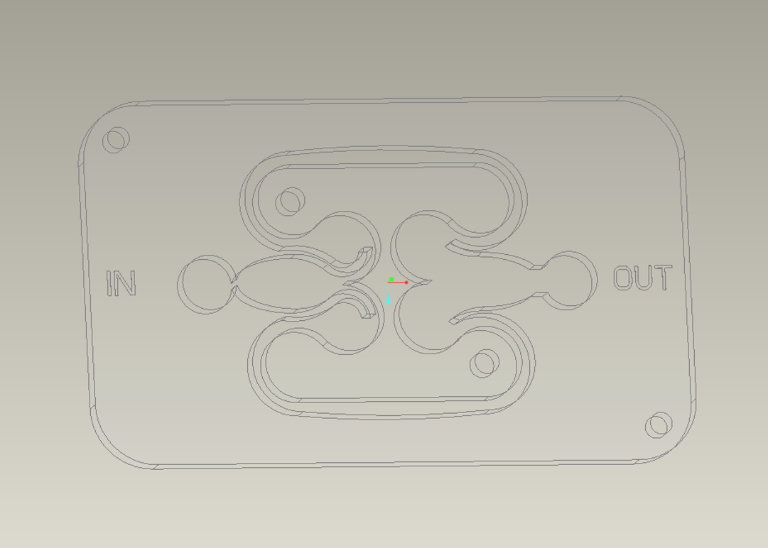
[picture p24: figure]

Figure 10: Couche central du mélangeur

Notre conception est basée sur un principe de sandwich, une première épaisseur permettant l’étanchéité, le support et le guidage des autres couches. Une couche centrale munit d’un détrompeur composer d’un élément externe guider par deux goupilles extérieures, et un élément interne guidé par les goupilles intérieures. Et enfin une dernière couche permettant de fermer le tout, toujours guider par les deux goupilles externes. L’adhésion et l’étanchéité sera assuré par une couche adhésive déposer sur les plaques.

Projet thématique MOON | AYRINHAC Elisa, DROUIN Clément, JOUCLARD Charly | 14

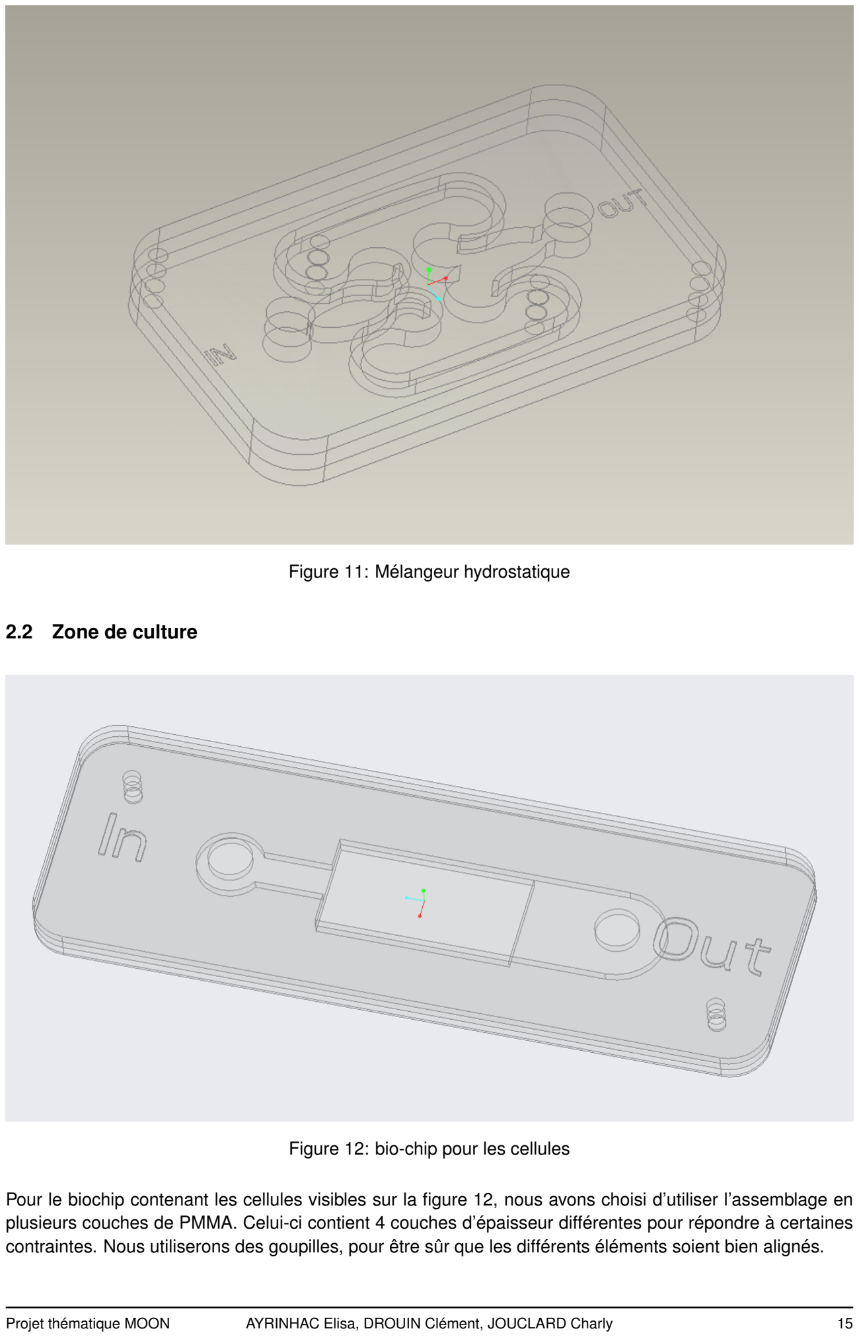
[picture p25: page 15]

Figure 11: Mélangeur hydrostatique

### 2.2 Zone de culture

Figure 12: bio-chip pour les cellules

Pour le biochip contenant les cellules visibles sur la figure 12, nous avons choisi d’utiliser l’assemblage en plusieurs couches de PMMA. Celui-ci contient 4 couches d’épaisseur différentes pour répondre à certaines contraintes. Nous utiliserons des goupilles, pour être sûr que les différents éléments soient bien alignés.

Projet thématique MOON | AYRINHAC Elisa, DROUIN Clément, JOUCLARD Charly | 15

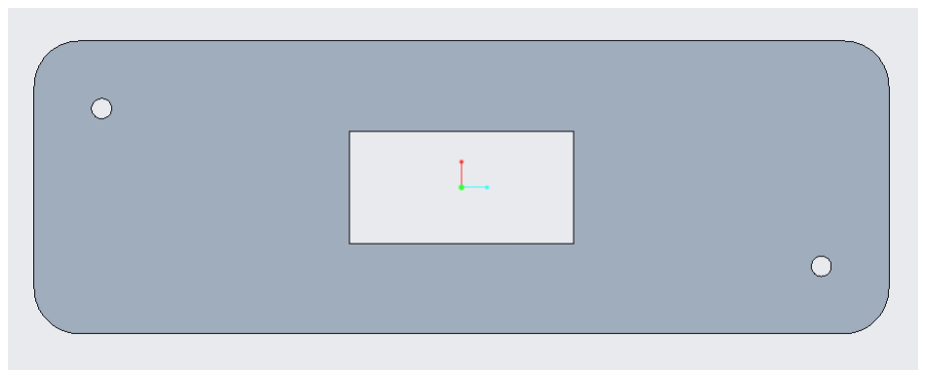
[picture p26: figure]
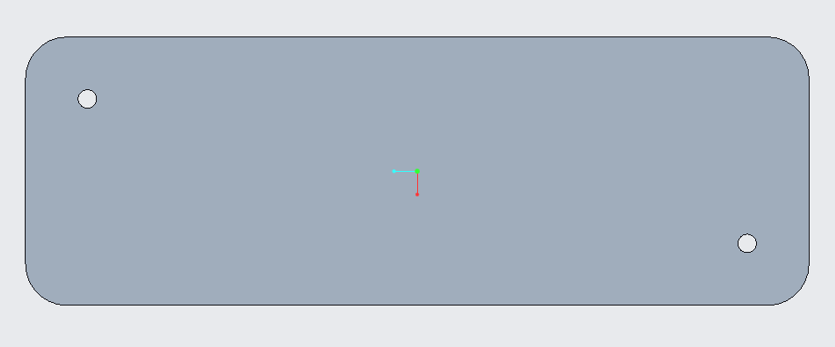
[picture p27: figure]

Figure 13: CAO de la première couche | Figure 14: CAO de la seconde couche

La couche du dessous fait 0.3 mm d’épaisseur pour permettre l’observation des cellules au microscope. La 2e couche est prévu pour contenir les cellules mais sera supprimer car elle crée des angles droits qui risque d’endommager les cellules.

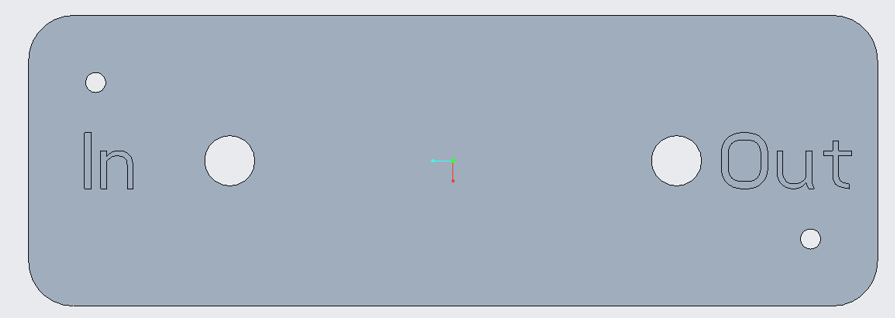
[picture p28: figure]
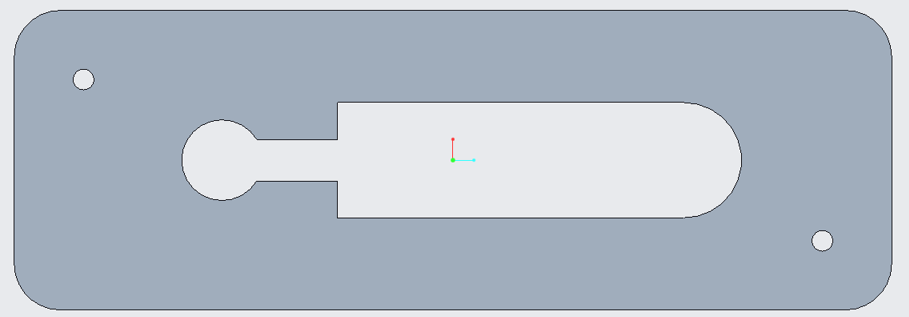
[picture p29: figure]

Figure 15: CAO de la troisième couche | Figure 16: CAO de la quatrième couche

La 3e couche permet au fluide contenant les hormones et nutriment de circuler la où seront accroché les cellules. L’entrée du fluide est plus étroite que la sortie pour éviter des problèmes de surpression. Et enfin la dernière couche contient les trous pour chasser les connecteur Luer lock, permettant de relier le bio chip contenant les cellules au reste du système par l’intermédiaire de tuyaux. Les angles devront être arrondit pour éviter d’endommager les cellules.

### 2.3 Support des réservoirs

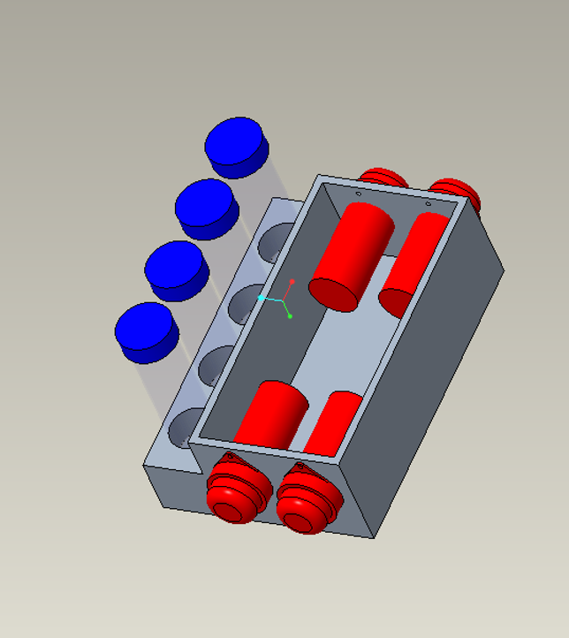
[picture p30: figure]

Figure 17: CAO du porte réservoir version 1


Figure 18: CAO du porte réservoir version 2

Projet thématique MOON | AYRINHAC Elisa, DROUIN Clément, JOUCLARD Charly | 16

Désormais nous avons une idée très claire du rendu physique du projet, celui-ci sera composer d’un boitier auxquelles sera fixé les trois pompe, les quatre tube comprenant les hormones, le liquide de culture neuf, et usagé. Ce boitier sera lui aussi découper au LASER et au besoin renforcé par des pièces imprimé en 3D. Il ne contiendra pas l’électronique, celui-ci sera placer en dehors de l’incubateur et relier au système via un câble. Il est à noter qu’il manque les électrovannes, qui ont été modéliser et qui seront placer de l’autre côté des pompes.


Figure 19: CAO des électrovannes

Projet thématique MOON | AYRINHAC Elisa, DROUIN Clément, JOUCLARD Charly | 17

## 3 Conception électronique et programmation

### 3.1 Carte d’alimentation

L’alimentation de tous le biochip se fera via l’alimentation d’un Arduino de 60 W. Il arrive sur la carte d’alimentation via la connectique circulaire JAlim. U1 est un régulateur de tension à découpage de la marque TRACO, il permet de descendre la tension de 12V à 5V il sert à alimenter le Raspberry pi qui sera alimenter par ses pins GPIO. Les moteurs seront contrôlés par les mosfet M1, M2 et M3. Les moteurs seront branchés à la carte via des connecteurs circulaire afin que le système soit le plus flexible possible. Les diodes D1, D2 et D3 sont des diodes de roues libres.

### 3.2 Programmation

### 3.2.1 GitHub

On a mis en place un GitHub pour se partager les codes de programmation, le "repo" contient aussi une ébauche du guide d’utilisateur. Le guide d’utilisateur contient actuellement uniquement les requirements pour le Raspberry pi ainsi que les commandes à utiliser.

### 3.2.2 Raspberry Pi

On a configuré le Raspberry pi 4 pour qu’on puisse se connecter dessus à distance à l’aide du protocole SSH. On peut s’y connecter facilement dessus à partir du moment que l’on se trouve sur le même réseau wifi. On peut lui transmettre des fichiers ainsi que récupérer des fichiers qui sont stockées dessus.

### 3.2.3 Préparation des données

Ce code permet de préparer les datas afin de pouvoir être utiliser par le logiciel qui contrôle le biochip. Il a été conçu pour que l’utilisateur rentre un minimum de donner afin de gagner du temps. Il permet de convertir un fichier csv que l’utilisateur aura créée au préalable avec les différents jalons de concentration en un fichier qui contient toutes les concentrations de l’expérience sur 28 jours. Sur la figure 20 on peut voir une représentation des données rentrées par l’utilisateur et les données produites par le programme.


Figure 20: Données généré par le programme avec les données rentrées par l’utilisateur

On peut l’utiliser directement sur un ordinateur puis envoyer le fichier généré sur le Raspberry pi ou bien on peut envoyer le fichier csv sur le Raspberry pi puis le généré directement sur le Raspberry pi. Le fichier

Projet thématique MOON | AYRINHAC Elisa, DROUIN Clément, JOUCLARD Charly | 18

généré est un fichier de type ftr il n’est donc pas lisible directement ceci est fait afin de gagner en rapidité d’exécution et gagner du stockage. Si on utilisait un fichier csv équivalent il contiendrait tellement de donnés qu’il faudrait plusieurs secondes pour le généré et il prendrait 10 fois plus de stockage. Le fichier à préparer doit être présenter sous la forme :

Time | Conc1 | Conc2
0 | 1 | 1
2 | 6 | 8
10 | 2 | 1
15 | 4 | 2
Projet thématique MOON | AYRINHAC Elisa, DROUIN Clément, JOUCLARD Charly | 19

## 4 Conclusion

Pour conclure on peut commencer la découpe du mélangeur et de la zone de culture afin de commencer les tests. Il faut commander les pièces électroniques pour commencer les tests électroniques.

Projet thématique MOON | AYRINHAC Elisa, DROUIN Clément, JOUCLARD Charly | 20

## 5 Annexe

Projet thématique MOON | AYRINHAC Elisa, DROUIN Clément, JOUCLARD Charly | 21

## References

[1] Welco. WPM peristaltic pump selection guide.
Projet thématique MOON | AYRINHAC Elisa, DROUIN Clément, JOUCLARD Charly | 22

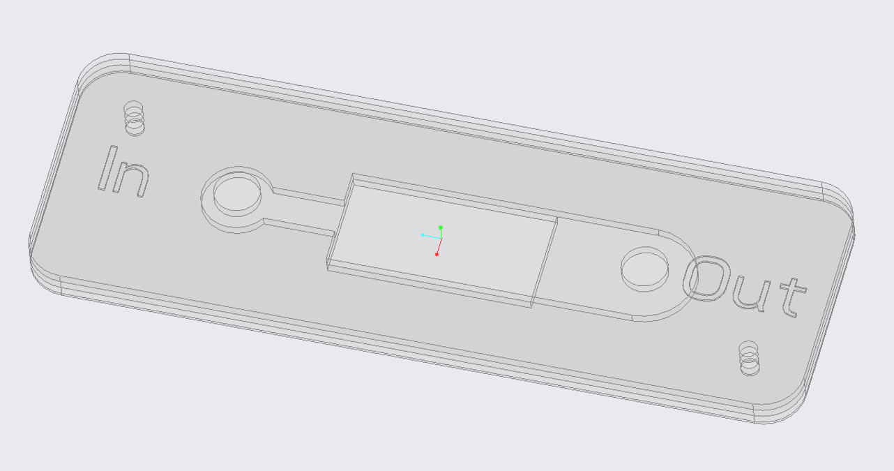
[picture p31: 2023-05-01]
rapport/figure/CAO_cellule.png

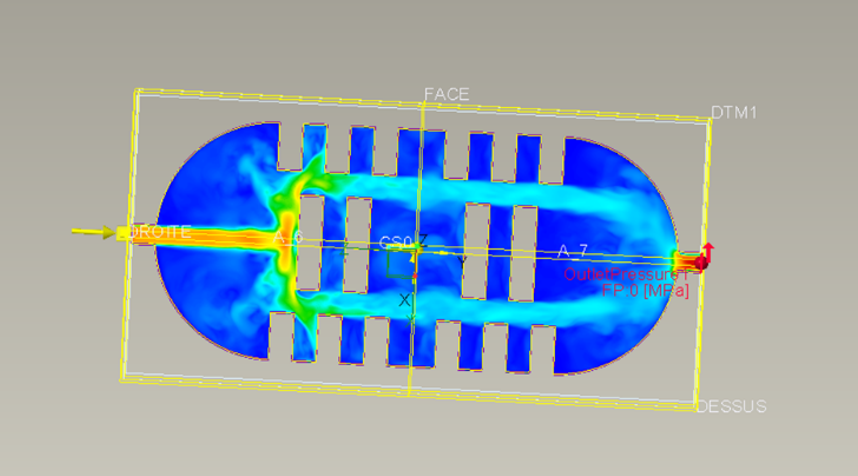
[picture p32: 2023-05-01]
rapport/figure/simulation3.png

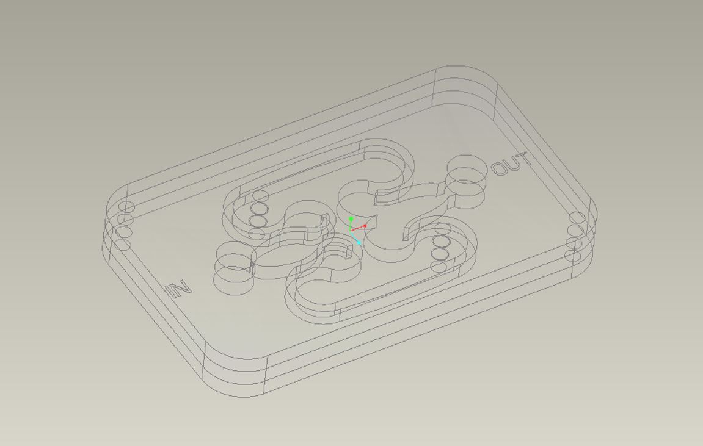
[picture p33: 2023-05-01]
rapport/figure/CAO_melangeur.png

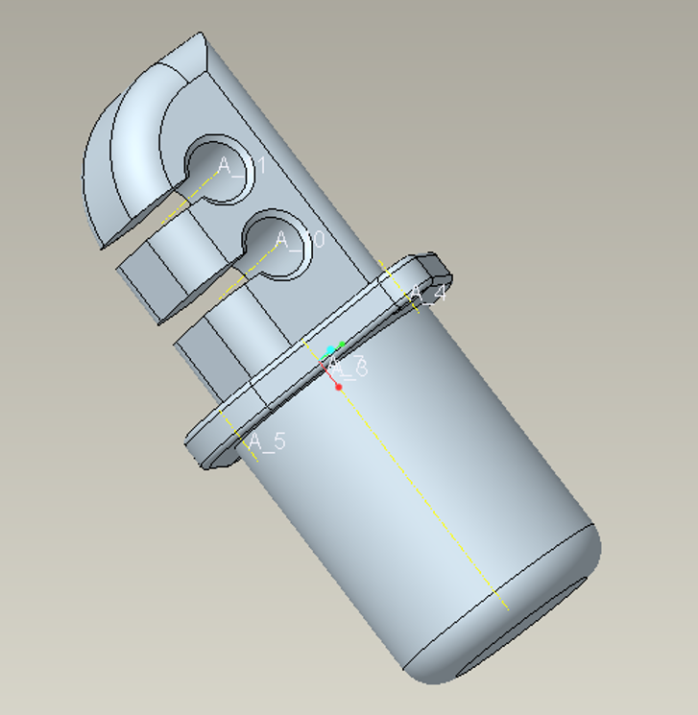
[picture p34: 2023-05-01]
rapport/figure/CAO_electrovanne.png

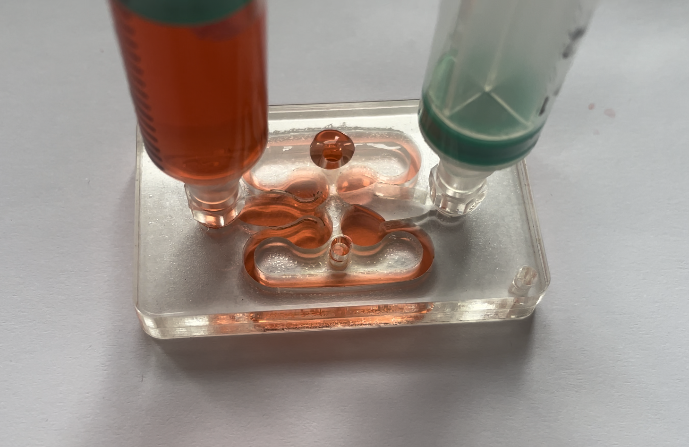
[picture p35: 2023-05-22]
rapport/figure/fuite_melangeur.PNG

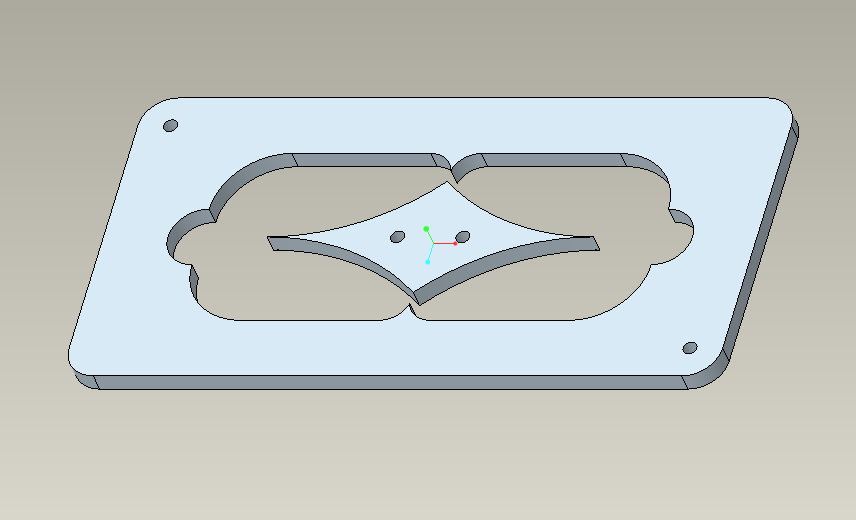
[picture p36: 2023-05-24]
rapport/figure/CAO_melangeur_V2_couche2.png

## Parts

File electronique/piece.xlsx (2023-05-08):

Pièce | Référence | Site | url | Quantité | Prix unitaire | Prix Lot | Total | 69.60 CHF
Mosfet | CSD18537NKCS | Digikey | https://www.digikey.fr/fr/products/detail/texas-instruments/CSD18537NKCS/4279645?s=N4IgTCBcDaIMIGUAiBGAHAVgMwHYByA0oiALoC%2BQA | 10 | 1.10 CHF | 10.96 CHF
Connectique male | PJ-002AH-SMT-TR | Digikey | https://www.digikey.fr/fr/products/detail/cui-devices/PJ-002AH-SMT-TR/408452?s=N4IgTCBcDaIAoCkC0AGFYCCAJJBlAsgCpKEBKIAugL5A | 10 | 1.15 CHF | 11.54 CHF
Régulateur | TSR 2-2450 | Digikey | https://www.digikey.fr/fr/products/detail/traco-power/TSR-2-2450/9383726?s=N4IgTCBcDaICoGUBKYC0YAsBWADCAugL5A | 1 | 10.66 CHF | 10.66 CHF
Pin | TMM-103-03-T-S | Digikey | https://www.digikey.fr/fr/products/detail/samtec-inc/TMM-103-03-T-S/2345216 | 4 | 0.41 CHF | 1.64 CHF
Resistance | RSMF1JT1K00 | Digikey | https://www.digikey.fr/fr/products/detail/stackpole-electronics-inc/RSMF1JT1K00/1694466 | 10 | 0.17 CHF | 1.71 CHF
Diode | SB5100-T | Digikey | https://www.digikey.fr/fr/products/detail/diodes-incorporated/SB5100-T/278636 | 10 | 0.54 CHF | 5.39 CHF
Connectique femelle | KLDX-PA-0202-A-LT | Digikey | https://www.digikey.fr/fr/products/detail/kycon-inc/KLDX-PA-0202-A-LT/9990091 | 10 | 2.77 CHF | 27.70 CHF

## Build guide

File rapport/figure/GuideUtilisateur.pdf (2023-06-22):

# Requirements :

For Raspberry pi

- Raspberry Pi OS Lite (64-bit)
- Python 3.10
- Python Libraries :
- numpy 1.22.2
- pandas 1.4.1
- feather-format 0.4.1

For Windows (optional)

- Python 3.10
- Python Libraries :
- numpy 1.22.2
- pandas 1.4.1
- feather-format 0.4.1
- matplotlib 3.5.2

# RaspberryPi recommendation :

- RaspberryPi type : RaspberryPi-4
- RaspberryPi name : raspberrypi-projetMOON
- piUser : projetMOON

# Useful command :

For windows with powershell :

- Connect to raspberryPi with SSH :
ssh piUser@piName
- Send file to raspberryPi :
scp dataToSend piUser@piName:/home/piUser/folderPath
- Retrieve file from raspberryPi :
scp piUser@piName:/home/piUser/FilePath localFilePath
if you are already in localFilePath, replace localFilePath by ".\"

For raspberry-pi terminal :

- View file in directory : ls
- change directory :
cd directoryName
if you want to go in parent folder change directoryName by ..
- remove file :
rm fileName
- read file :
cat fileToRead
- start pyhton script
python script.py
- start experience script
nohup python experience.py ftrFile.ftr

# How to setup your raspberry-pi :

You need to use the Raspberry Pi Imager software available here
: https://www.raspberrypi.com/software/

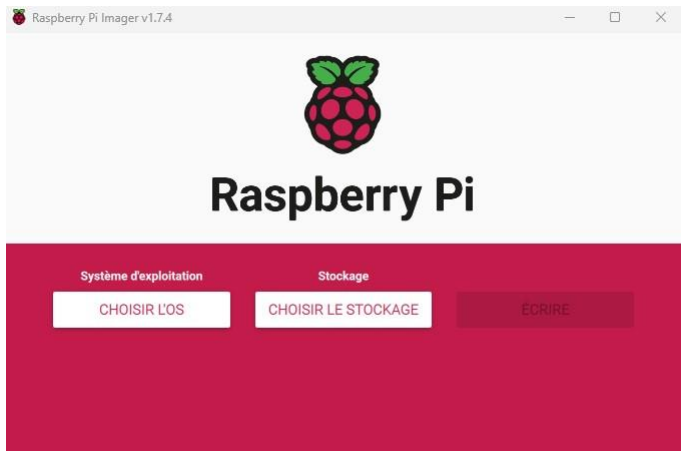
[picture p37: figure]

## Step 1 : Choose OS

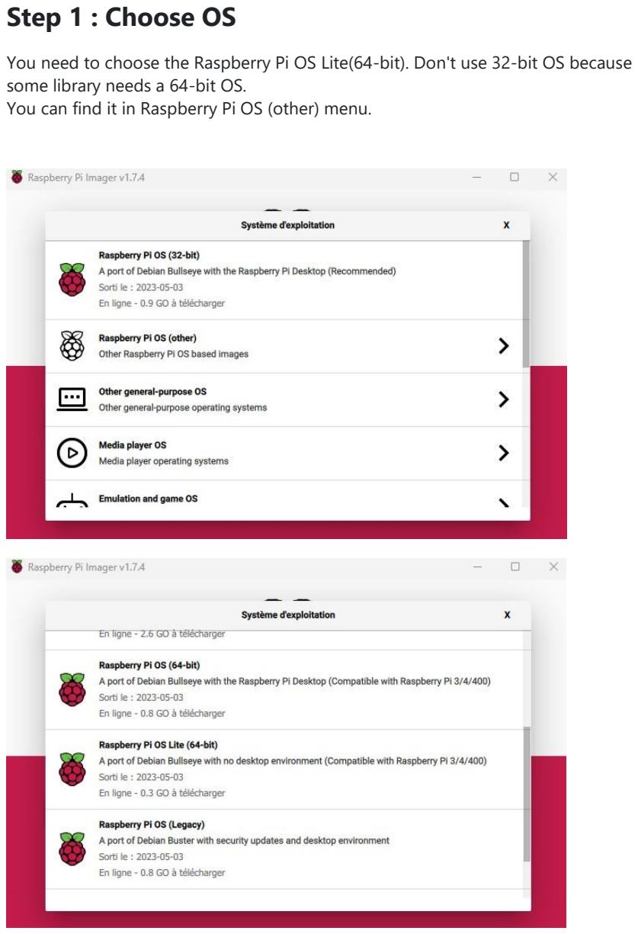
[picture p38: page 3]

You need to choose the Raspberry Pi OS Lite(64-bit). Don't use 32-bit OS because some library needs a 64-bit OS.
You can find it in Raspberry Pi OS (other) menu.

## Step 2 : Chose storage

Select the SD card you will use for the raspberry pi.

## Step 3 : Setup advance parameter

You need to change multiple parameter before writing the OS in the SD card : You can find the parameter in the gear.

- Chose for all sessions in Image customization options
- Change the raspberry pi name
- Activate SSH :
use authentification by password
- Define username and password
- Configurate the wifi

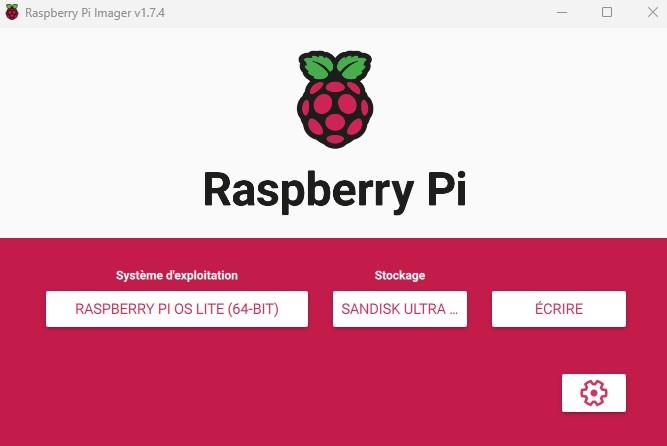
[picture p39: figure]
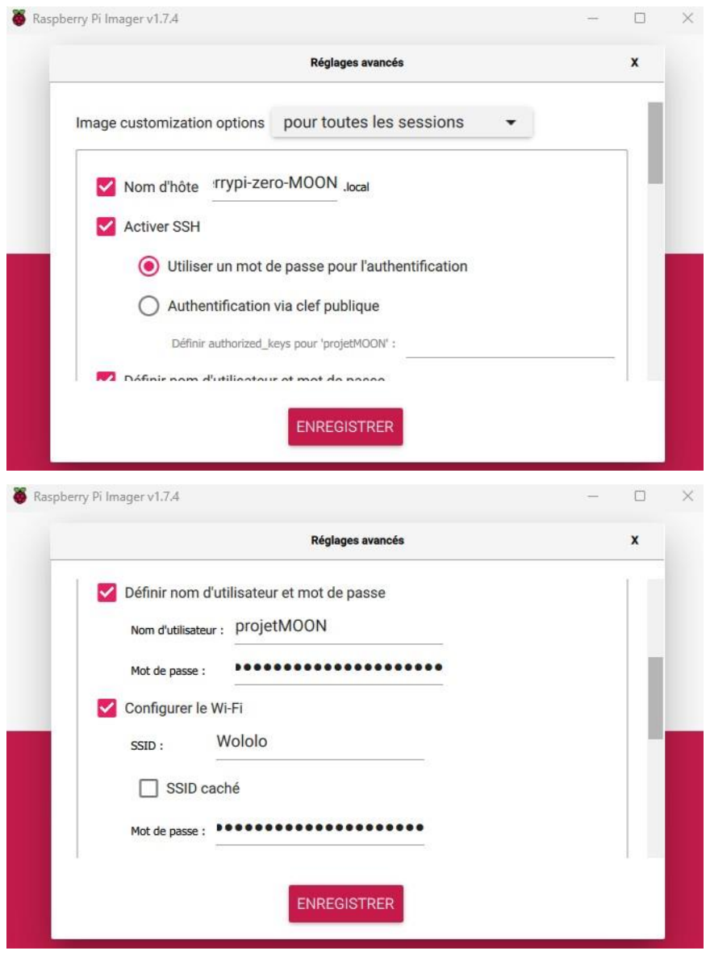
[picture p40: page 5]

## Step 4 : Write on SD card

You can write the OS in the SD card and your OS it's ready !

## Step 5 : Install dependencies and Setup directory

You need to install dependencies.

- Connect to your raspberry pi via SSH :
ssh piUser@piName
use the piUser and piName you have setup in step 3.
- Install OS update :
sudo apt update
sudo apt upgrade
- Install python :
sudo apt install python3.10
- Install python library :
pip install numpy
pip install pandas
pip install feather-format
- Create directory :
mkdir data
mkdir userData

All the dependencies are installed you can close the SSH connection by closing the terminal.

## Step 6 : Transfert file on raspberry pi

You need to transfert all necessary file on raspberry pi. Download following file from the repository :

- armerPompe.py
- controle.csv
- controle.py
- dataPreparation.py
- experience.py
- resetGPIO.py

repeat the following command for each file in the list to transfert to raspberry pi :

- Send file to raspberryPi :
scp fileToSend piUser@piName:/home/piUser

The setup of the raspberry pi is complete.

# Plug experience

## Motor

### Motor n°1

- red wire to Mosfet 1 Drain
- black wire to Mosfet 1 Source

### Motor n°2

- red wire to Mosfet 2 Drain
- black wire to Mosfet 2 Source

### Motor n°3

- red wire to Mosfet 3 Drain
- black wire to Mosfet 3 Source

## Electrovanne

### Electrovanne n°1

- wires to Mosfet 4 Drain/Source

### Electrovanne n°2

- wires to Mosfet 5 Drain/Source

### Electrovanne n°3

- wires to Mosfet 5 Drain/Source

## Raspberry pin

### Alimentation

- pin 4 (Alimentation 5V) to 5 V
- pin 6 (GND) to GND

### Motor

- pin 11 (GPIO 17) to Mosfet 1 Gate
- pin 13 (GPIO 27) to Mosfet 2 Gate
- pin 15 (GPIO 22) to Mosfet 3 Gate

### Electrovanne

- pin 29 (GPIO 5) to Mosfet 4 Gate
- pin 31 (GPIO 6) to Mosfet 5 Gate
- pin 33 (GPIO 13) to Mosfet 6 Gate

# Run an experience

## Step 1 : Prepare your data

The data need to be in csv file. The separator need to be ",". Your data are presented like this :

time | conc1 | conc2
0 | 1 | 1
2 | 6 | 8
10 | 2 | 1
15 | 4 | 2

time correspond of time from the start in second.
conc1 and conc2 it's the concentration of element at time t.

If you have download dataPreparation.py on your computer you can convert your data on your computer directly. For convert your data directly on your computer follow the Step 3 before the Step 2.

## Step 2 : Transfert your data on raspberry pi

Transfert your data on the raspberry pi in the folder userData.
Open terminal in the folder of your data and use this command :
scp dataToSend piUser@piName:/home/piUser/userData
If you have convert your data directly on your computer use this command instead : scp dataToSend piUser@piName:/home/piUser/data

## Step 3 : Convert your data

### If you have transfert your CSV file on raspberry pi

- Connect to your raspberry pi via SSH :
ssh piUser@piName
- run dataPreparation.py :
python dataPreparation.py
Indicate the name of your data when ask.

Your data is now converted and placed in data.
The data converted is named by the date of creation like this: year-moth-day_hourminsec.ftr

you can check the name of the data created in the folder data using : cd data
ls
it will show all the data in the folder data.

### If you want convert your data on Windows

Before convert your data on Windows make sure you have the optionnal requirement on your computer.
Create 2 folder in directory of dataPreparation.py:
- userData
- data

Put your data to convert in userData folder.
Run dataPrepartion.py and indicate the name of your data when ask. Your data is now converted and placed in data.
The data converted is named by the date of creation like this: year-moth-day_hourminsec.ftr
You can check the data created using the script verificationFtr.py Now you can do Step 2.

## Step 4 : Run experience

For start experience connect to raspberry pi if it's not already done : ssh piUser@piName
Run experience.py in background with :
nohup python experience.py dataToUse.ftr
Close the terminal.
The Experience is running Step 5 and 6 will show you how to interact with experience.

## Step 5 : Control experience

If you want take sample or make an observation during the experience you need to suspend the process.

- Connect to raspberry pi :
ssh piUser@piName
- run controle.py python controle.py

- Choose what you want to do :
i. Sample
For take a sample, you need to indicate which quantity you take.
ii. | Observation For observe the cells.
iii. | Restart cycle When you have finished your sample/observation restart the cycle.
iv. | Log For see the last log of the experience.
v. Stop
| Force stop of the experience if something goes wrong.
vi. | Cancel Close controle.py

When you have finished dont forget to restart cycle and you can press cancel for close controle.py

## Step 6 : Check log

- Connect to raspberry pi : ssh piUser@piName
- Open the log:
cat output.log

For debug log use instead : cat nohup.out

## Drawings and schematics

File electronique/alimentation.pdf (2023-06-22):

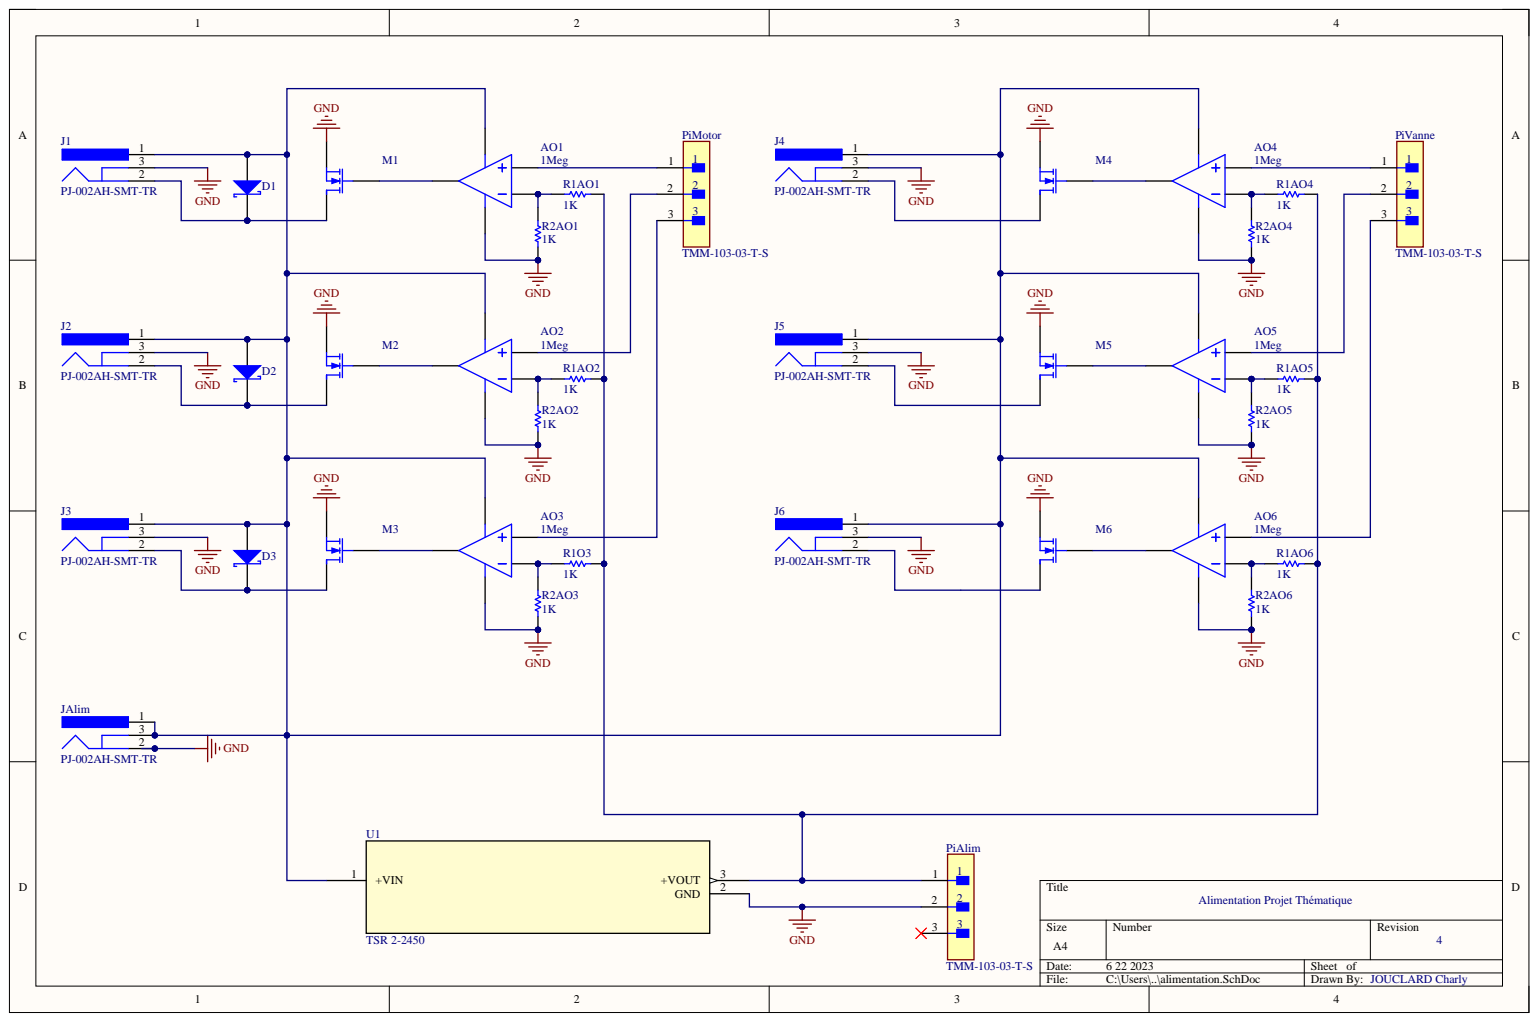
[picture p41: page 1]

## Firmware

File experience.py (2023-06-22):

import pandas as pd
import os
import sys
import threading
import time
import RPi.GPIO as GPIO

outputFileName = "output.log"
outputFilePath = "./"+outputFileName
controleFile = "./controle.csv"
concentrationFile = ""
concentrationFilePath = "./data/"


class Pompe():
    debit = 0
    id = ""
    pinNumber = 0
    
    def __init__(self,newDebit,newId, newPin):
        self.debit = newDebit
        self.id = newId
        self.pinNumber = newPin

    def injection(self,quantity):

        #TURN ON PUMP
        GPIO.output(self.pinNumber,GPIO.HIGH)
        time.sleep(self.timeToRun(quantity))
        GPIO.output(self.pinNumber,GPIO.LOW)
        #TURN OFF PUMP

    def timeToRun(self,quantity):
        return int((quantity/self.debit)*60)
    
    def on(self):
        GPIO.output(self.pinNumber,GPIO.HIGH)
    def off(self):
        GPIO.output(self.pinNumber,GPIO.LOW)

class Electrovanne():
    id = ""
    pinNumber = 0

    def __init__(self,id,newPin):
        self.id = id
        self.pinNumber = newPin

    def on(self):
        GPIO.output(self.pinNumber,GPIO.HIGH)

    def off(self):
        GPIO.output(self.pinNumber,GPIO.LOW)

class Tee(object):
    def __init__(self, file_name=outputFileName):
        self.file = open(file_name, "a")

    def __enter__(self):
        self.stdout = sys.stdout
        sys.stdout = self

    def __exit__(self, exc_type, exc_value, traceback):
        sys.stdout = self.stdout
        self.file.close()

    def write(self, message):
        self.file.write(message)
        self.file.flush()
        self.stdout.write(message)

updateConcentration = False
isSuspended = False
isStop = False

timeBetweenChange = 30
volumeTotal = 10.0
startTime = 0

scheduleConcentration = None

pinPompe = [17,27,22]
pinVanne = [5,6,13]
debitPompe = [1.0549,1.3314,1.3197]
listePompe = [Pompe(debitPompe[0],"conc1",pinPompe[0]),Pompe(debitPompe[1],"conc2",pinPompe[1]),Pompe(debitPompe[2],"flow",pinPompe[2])]
listeVanne = [Electrovanne("purge",pinVanne[0]),Electrovanne("cells",pinVanne[1]),Electrovanne("nut",pinVanne[2])]

lastNutConc = 0
lastConc1 = 0
lastConc2 = 0

def checkOs():
    """
    Check system OS if windows change path syntax
    """
    global outputFileName
    global outputFilePath
    global controleFile
    global concentrationFilePath
    if os.name == "nt":
        outputFilePath = ".\\"+outputFileName
        controleFile = ".\\controle.csv"
        concentrationFilePath = ".\\Data\\"

def getArg():
    """
    Get argument when you start the script
    """
    global concentrationFilePath
    global concentrationFile
    global timeBetweenChange

    if len(sys.argv) == 1:
        with Tee():
            print("Please indicate which data you would use.")
    
    elif len(sys.argv) == 2:
        try:
            concentrationFile = pd.read_feather(concentrationFilePath+sys.argv[1])
            with Tee():
                print(getTime()+"|"+"Start sequence with file "+sys.argv[1])
            return True
        except:
            with Tee():
                print("Unable to open concentration file")
            return False
    
    elif len(sys.argv) == 3:
        #For debug only
        if sys.argv[2] == "debug":
            try:
                with Tee():
                    print("=========Debug mode=========")
                    print(getTime())
                return False
            except:
                with Tee():
                    print("Unable to open concentration file")
                return False
        elif sys.argv[2] == "demo":
            #For demo only
            try:
                concentrationFile = pd.read_feather(concentrationFilePath+sys.argv[1])
                timeBetweenChange = 5
                with Tee():
                    print(getTime()+"|""Start sequence with file "+sys.argv[1]+" for demo")
                return True
            except:
                with Tee():
                    print("Unable to open concentration file")
                return False
        else:
            with Tee():
                print("I don't understand")
            return False
    
    else:
        with Tee():
            print("Too many argument. I take only 1 argument. 2 For debug only.")
        return False
    
def getTime():
    actualDate = time.localtime()
    if actualDate.tm_mday < 10:
        day = "0"+str(actualDate.tm_mday)
    else:
        day = str(actualDate.tm_mday)

    if actualDate.tm_mon < 10:
        month = "0"+str(actualDate.tm_mon)
    else:
        month = str(actualDate.tm_mon)

    if actualDate.tm_hour < 10:
        hour = "0"+str(actualDate.tm_hour)
    else:
        hour = str(actualDate.tm_hour)

    if actualDate.tm_min < 10:
        minute = "0"+str(actualDate.tm_min)
    else:
        minute = str(actualDate.tm_min)

    dateToReturn = day+"."+month+"."+str(actualDate.tm_year)+" : "+hour+"h"+minute+"min"
    return dateToReturn

def removeLine():
    """
    Remove the first line of controlFile
    """
    global controleFile
    with open(controleFile, 'r+') as file:
        # read an store all lines into list
        lines = file.readlines()
        # move file pointer to the beginning of a file
        file.seek(0)
        # truncate the file
        file.truncate()
        file.writelines(lines[1:])

def getFirstLine():
    """
    Return the first line of controlFile
    """
    global controleFile
    with open(controleFile,"r") as file:
        line = file.readline()
        return line[:len(line)-1]

def prepareAction(line):
    """
    Prepare action to do
    """
    commaIndex = line.find(";")
    actionToDo = line[:commaIndex]
    argument = line[commaIndex+1:]
    return actionToDo, argument

def doAction(actionToDo, argument):
    """
    Do action. List of action : Prelevement, Observation, Reprendre cycle, Stop
    """
    global isSuspended
    global isStop
    global volumeTotal

    #Prelevement : Isolate Cells, Remove x ml from circuit, Pause cycle
    if actionToDo == "Sample":
        isSuspended = True
        volumeTotal = volumeTotal-int(argument)
        for vanne in listeVanne:
            if vanne.id=="cells":
                vanne.off()
        with Tee():
                print(getTime()+"|"+"You can take your sample")
    #Observation : Isolate Cells, Pause cycle
    elif actionToDo == "Observation":
        isSuspended = True
        for vanne in listeVanne:
            if vanne.id=="cells":
                vanne.off()
        with Tee():
                print(getTime()+"|"+"You can do your observation")
    #Reprendre cycle : Open cells, restart cycle
    elif actionToDo == "Resume_cycle":
        isSuspended = False
        for vanne in listeVanne:
            if vanne.id=="cells":
                vanne.on()
        with Tee():
                print(getTime()+"|"+"Restarting cycle")
    #Stop script
    elif  actionToDo == "Stop":
        isStop = True

def getConc():
    """
    Get concentratoion from ftr file
    """
    global startTime
    timeInSecond = int((time.monotonic()-startTime))
    conc1 = concentrationFile["Conc1"].iloc[timeInSecond]
    conc2 = concentrationFile["Conc2"].iloc[timeInSecond]
    nutConc = 100.0 - conc1 - conc2
    nutConc = nutConc / 100
    conc1 = conc1 / 100
    conc2 = conc2 / 100
    return nutConc,conc1,conc2

def startPurge(purgeTime):
    """
    Purge the system
    """
    for vanne in listeVanne:
        vanne.on()

    with Tee():
        print(getTime()+"|"+"Starting purge")

    time.sleep(purgeTime)

    with Tee():
        print(getTime()+"|"+"Purge finished")

    for vanne in listeVanne:
        vanne.off()

def purge(concentration_c1_mtn,concentration_c2_mtn, concentration_c1_apres, concentration_c2_apres, volume_circuit ):
    concentration_nut_mtn=1-concentration_c1_mtn-concentration_c2_mtn
    concentration_nut_apres=1-concentration_c1_apres-concentration_c2_apres
    volume_min = 3 # le volume mini a avoir sur le circuit
    purge=False
    volume_purge=0.0
    if (concentration_nut_apres <=concentration_nut_mtn):
       purge=False
       volume_purge=0.0 
    elif (concentration_nut_apres > concentration_nut_mtn):
        volume_mtn_nut = concentration_nut_mtn*volume_circuit
        volume_mtn_c1 = concentration_c1_mtn*volume_circuit
        volume_mtn_c2 = concentration_c2_mtn*volume_circuit
        
        volume_apres_nut = concentration_c1_apres*volume_min
        volume_apres_c1 = concentration_c2_apres*volume_min
        volume_apres_c2 = concentration_nut_apres*volume_min
        
        volume_pour_purge=0
        
        volume_reste_purge_nut = volume_mtn_nut-(volume_pour_purge*concentration_nut_mtn)
        volume_reste_purge_c1 = volume_mtn_c1-(volume_pour_purge*concentration_c1_mtn)
        volume_reste_purge_c2 = volume_mtn_c2-(volume_pour_purge*concentration_c2_mtn)
        volume_tot_reste_purge = volume_circuit-volume_pour_purge
        
        
        while (volume_reste_purge_nut>volume_apres_nut or volume_reste_purge_c1>volume_apres_c1 or volume_reste_purge_c2>volume_apres_c2):
            
            volume_reste_purge_nut = volume_mtn_nut-(volume_pour_purge*concentration_nut_mtn)
            volume_reste_purge_c1 = volume_mtn_c1-(volume_pour_purge*concentration_c1_mtn)
            volume_reste_purge_c2 = volume_mtn_c2-(volume_pour_purge*concentration_c2_mtn)
            volume_tot_reste_purge = volume_circuit-volume_pour_purge
            volume_pour_purge=volume_pour_purge+1
            
        
        if (volume_tot_reste_purge<volume_min):
            volume_pour_purge=volume_circuit-volume_min
            
        
        purge=True
        volume_purge=round(volume_pour_purge,2)
            
    return purge, volume_purge
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

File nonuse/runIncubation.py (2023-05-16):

import os
import sys
import numpy as np
import pandas as pd
import RPi.GPIO as GPIO

dataFolder = "data"
dataPath = "./"+dataFolder+"/"

def checkFolder(folder):
    """
    Check if folder exist if not create it.
    return true if exist, if not return false
    """
    if not os.path.isdir(folder):
        print(dataFolder, "folder was not found. Run dataPreparation.py to prepare your data.")
        sys.exit(0)
    else:
        pass

def setupPWM(pinMotor:list,pinVanne:list):
    """
    Setup GPIO PWM with a frequency of 10Hz
    """
    frequencyPWM = 10
    moteur = [GPIO.PWM(pinMotor[0],frequencyPWM),GPIO.PWM(pinMotor[1],frequencyPWM),GPIO.PWM(pinMotor[2],frequencyPWM)]
    vanne = [GPIO.output(pinVanne[0],GPIO.HIGH),GPIO.output(pinVanne[1],GPIO.HIGH),GPIO.output(pinVanne[2],GPIO.HIGH)]
    return moteur,vanne

def setupGPIO():
    """
    Setup GPIO for control
    """
    #Pompe
    GPIO.setmode(GPIO.BCM)
    GPIO.setup(17, GPIO.OUT)
    GPIO.setup(27, GPIO.OUT)
    GPIO.setup(22, GPIO.OUT)
    #Electrovanne
    GPIO.setup(5, GPIO.OUT)
    GPIO.setup(6, GPIO.OUT)
    GPIO.setup(13, GPIO.OUT)

def testPWM(isMotor:bool,index:int,dutyCycle:float):
    """
    DO NOT USE ! FOR DEBUG ONLY !
    index : 0,1 or 2
    dutyCycle : 0.0<dc<100.0
    """
    if isMotor:
        motor[index].start(dutyCycle)
        input('Press return to stop:')   # use raw_input for Python 2
        motor[index].stop()
    else:
        vanne[index].start(dutyCycle)
        input('Press return to stop:')   # use raw_input for Python 2
        vanne[index].stop()

def endProgram():
    """
    Clean all GPIO used for clean ending
    """
    GPIO.cleanup()
'''
servo_pin = 18  # équivalent de GPIO 18
GPIO.setmode(GPIO.BCM)  # notation BCM
GPIO.setup(servo_pin, GPIO.OUT)  # pin configurée en sortie
pwm = GPIO.PWM(servo_pin, 50)  # pwm à une fréquence de 50 Hz
rapport = 7       # rapport cyclique initial de 7%
pwm.start(rapport)
pwm.ChangeDutyCycle(float(rapport))
'''

checkFolder(dataFolder)
setupGPIO()
motor,vanne = setupPWM([17,27,22],[5,6,13])
for i in range(0,3):
    testPWM(True,i,50)
for i in range(0,3):
    testPWM(False,i,50)
endProgram()

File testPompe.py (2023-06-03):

import asyncio
import time
import RPi.GPIO as GPIO


electrovanne = [5,6,13]
testPompe = []
testElectroVanne = []
isRunning = True
nextMenu = 1

def setupPWM(pinMotor:list):
    """
    Setup GPIO PWM with a frequency of 0.1Hz
    """
    frequencyPWM = 100
    moteur = [GPIO.PWM(pinMotor[0],frequencyPWM),GPIO.PWM(pinMotor[1],frequencyPWM),GPIO.PWM(pinMotor[2],frequencyPWM)]
    return moteur

def setupGPIO():
    """
    Setup GPIO for control
    """
    GPIO.setmode(GPIO.BCM)
    #Moteur
    GPIO.setup(17, GPIO.OUT)
    GPIO.setup(27, GPIO.OUT)
    GPIO.setup(22, GPIO.OUT)
    
    #Electrovanne
    GPIO.setup(5, GPIO.OUT, initial=GPIO.LOW)
    GPIO.setup(6, GPIO.OUT, initial=GPIO.LOW)
    GPIO.setup(13, GPIO.OUT, initial=GPIO.LOW)

def endProgram():
    """
    Clean all GPIO used for clean ending
    """
    global motor
    global electrovanne
    for i in range(0,3):
        motor[i].stop()
        GPIO.output(electrovanne[i],GPIO.LOW)

def checkInput(userInput,menu=0):
    try:
        userInput = int(userInput)
        if menu == 0:
            #menu0
            if userInput>0 and userInput<5:
                return False,userInput
            else:
                raise
        elif menu == 1:
            #index
            if userInput>-1 and userInput<3:
                return False,userInput
            else:
                raise
        elif menu == 2:
            #dc
            if userInput>=0 and userInput<=100:
                return False,userInput
            else:
                raise
        elif menu == 3:
            #timeRun
            if userInput>0 and userInput<=120:
                return False,userInput
            else:
                raise
        else:
            raise
    except:
        print("Je n'ai pas compris votre commande")
        return True

def getInput(menu=0):
    isWrongInput = True
    while isWrongInput:
        userInput = input()
        isWrongInput, userInput = checkInput(userInput,menu)
    return userInput
    
async def menu0():
    global nextMenu
    print("Que voulez vous tester ? :")
    print("1. Tout\n2. Moteur\n3. Electrovanne\n4. Fin du test")
    nextMenu = getInput(0)
    

async def menu1():
    print("dutyCycle à utiliser ?")
    dc = getInput(2)
    print("Pendant combien de temps ?")
    timeRun = getInput(3)
    taskTestAll = asyncio.create_task(testAll(dc,timeRun))
    await taskTestAll

async def menu2():
    print("Quelle pompe voulez vous tester (0,1,2)? :")
    index = getInput(1)
    print("dutyCycle à utiliser ?")
    dc = getInput(2)
    print("Pendant combien de temps ?")
    timeRun = getInput(3)
    taskTestPompe = asyncio.create_task(runPompe(index,dc,timeRun))

async def menu3():
    print("Quelle electrovanne voulez vous tester (0,1,2)? :")
    index = getInput(1)
    print("Pendant combien de temps ?")
    timeRun = getInput(3)
    taskTestElectrovanne = asyncio.create_task(runPompe(index,timeRun))
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

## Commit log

2023-03-07 first commit
    create folder for user data
    add dataPreparation script
    add test userData csv file
    [wololo.csv]
2023-05-05 Add BOM
    [piece.xlsx]
2023-05-08 update piece
    [piece.xlsx]
2023-05-12 add testPompe.py
    Add script for testing pump
    [ControlePompe.xlsx]
2023-05-24 Modif partie Clément
    Modification partie melangeurV2, ajout d'images de CAO.
    Ajout de deux sous-sous-parties : boitier à découper au LASER V1
    boitier à découper au LASER V2
    (version avec le nouveau mélangeur)
2023-05-25 update rapport.tex
    Ajout différents schéma électrique et prototype électronique
2023-05-25 update rapport.tex
    ajout de partie pour la programmation, amélioration de la conclusion
2023-05-26 TEST pompe
    [ControlePompe.xlsx]
2023-05-30 add command.py and log.csv
    update dataPreparation.py :
    - explicit global variable
    Add log.csv :
    -log will be control final script and will be a log
    Modify test.py
    -test for final script
    [log.csv]
2023-06-02 New control systeme
    [command.csv]
2023-06-07 patch dataPreparation.py
    dataPreparation.py
    -patch/optimisation interpolation des points
    mainTest.py
    -ajout lecture argument lors du lancement
    simulation.csv
    -ajout de l'entrée utilisateur final
    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
    [simulation.csv, wololo.csv]
2023-06-13 Modif LateX intro
    + gestion concentration
    3 print
2023-06-16 modif mainttest et rapport
    c/100 sur main
    modif intro rapport et correction faute intro arrêt avant état de l'art
2023-06-17 modif rapport
    modif etat de l'art rapport
2023-06-21 update program
    [demo.csv]
2023-06-22 fixed experience.py
    [demo.csv]
2023-06-22 move file
    [ControlePompe.xlsx, alimentation.SchDoc]
